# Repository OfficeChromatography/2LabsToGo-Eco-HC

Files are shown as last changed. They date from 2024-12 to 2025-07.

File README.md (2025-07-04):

# 2LabsToGo-Eco-HC

<u>Reference:</u> Schwack, W., Schmidt, J., Nimmerfroh, T. et al. Do-it-yourself, stand-alone, 
open-source nebulizer for derivatizations and bioassays in planar chromatography. 
JPC-J Planar Chromat (2025). https://doi.org/10.1007/s00764-025-00358-8

The repository contains the files for upgrading 2LabsToGo-Eco
 (https://github.com/OfficeChromatography/2LabsToGo-Eco) for Humidity Control.

## Downloading 2LabsToGo-Eco-HC
On the Raspberry Pi, open a new terminal and change to the directory Downloads
```bash
	cd ~/Downloads
```
Clone the 2LabsToG-Eco-HC repository from Github
```
	sudo git clone https://github.com/OfficeChromatography/2LabsToGo-Eco-HC.git
````

## Updating the firmware
The Marlin firmware and a built hex file are available in the folder Firmware-update.<br>
Copy the firmware hex file (firmware_2LabsToGo-Eco.hex) to the folder 2LabsToGo-Eco-Firmware.
```
	sudo cp -R ~/Downloads/2LabsToGo-Eco-HC/Firmware-update ~/2LabsToGo-Eco/2LabsToGo-Eco-Firmware
````
Change to the firmware folder
```
	cd ~/2LabsToGo-Eco/2LabsToGo-Eco-Firmware
````
Place the 2x4 jumper block onto the "ISP to PI" pins of the mainboard!<br> <br>
Execute the avrdude command
```
	sudo avrdude -p atmega2560 -C avrdude_gpio.conf -c 2LabsToGo -v -U flash:w:firmware_2LabsToGo-Eco.hex:i
````
Remove the jumper block from the "ISP to Pi" pins.<br>

## PID Tuning
After flashing the new firmware, the PID tuning must be performed again:<br>
•	In the software (Connection tab), connect the board.<br>
•	Insert the multifunctional plateholder and connect the plug.<br>
•	Connect the Mini-Incubator to the board.<br>
•	Send the following Gcodes and wait for finishing the tuning process
````
	M303 E-1 C8 S90 U  (for plateholder)
	M303 E0 C8 S40 U  (for Mini-Incubator)
````

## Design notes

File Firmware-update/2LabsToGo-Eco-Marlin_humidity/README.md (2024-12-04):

# OC-Control 
A Marlin 2.0 3D Printer based Firmware

## Marlin 2.0

Marlin 2.0 takes this popular RepRap firmware to the next level by adding support for much faster 32-bit and ARM-based boards while improving support for 8-bit AVR boards. Read about Marlin's decision to use a "Hardware Abstraction Layer" below.

Download earlier versions of Marlin on the [Releases page](https://github.com/MarlinFirmware/Marlin/releases).

## Building OC-Control

To build OC-Control [PlatformIO](http://docs.platformio.org/en/latest/ide.html#platformio-ide) is preferred. Detailed build and install instructions are posted at:

  - [Installing Marlin (VSCode)](http://marlinfw.org/docs/basics/install_platformio_vscode.html).

If you need more help, follow our [instruction_visualstudio-code](https://github.com/OfficeChromatography/OCLab3/blob/master/instruction_visualstudio-code.pdf), available above in the OCLab3 folder.

# OC-Manager 3 SOFTWARE
OC-Manager 3 installation 
[OC-Manager3](https://github.com/OfficeChromatography/OCLab3-Software)

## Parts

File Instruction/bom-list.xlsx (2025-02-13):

Parts | Amount | Exemplary seller | Euro (+VAT)
Fan MECHATRONICS MD4028V12B-RSR, 12VDC, 40mm L x 40mm H, 24.3cfm (0.680m³/min) (Digikey No. 1570-1126-ND) | 1 | Digikey | 11.31
Jumper Wire Male to Female 12.00" (304.80mm) 26 AWG, pack of 10, diff. colors (Digikey No. 2183-4567-ND) | 1 | Digikey | 2.81
Plexiglas 215 mm x 190 mm x 3 mm (front_215x190.dxf) | 1 | kunstoffplattenonline.de | 5.00
Round magnets, Ø 8 mm x 3 mm | 10 | supermagnete.de | 4.45
Superglue | 1 | local workshop | 4.90
Screw M3x40 | 4 | local workshop | 0.80
Nut M3 | 4 | local workshop | 0.60
Double-Sided Adhesive Tape tape, 6 mm, 50 cm needed | 1 | local workshop | 6.50
Eurostyle terminal strip with screws, 0.5 - 1.5 mm2 | 1 | local workshop | 2.00
 |  |  | 38.37

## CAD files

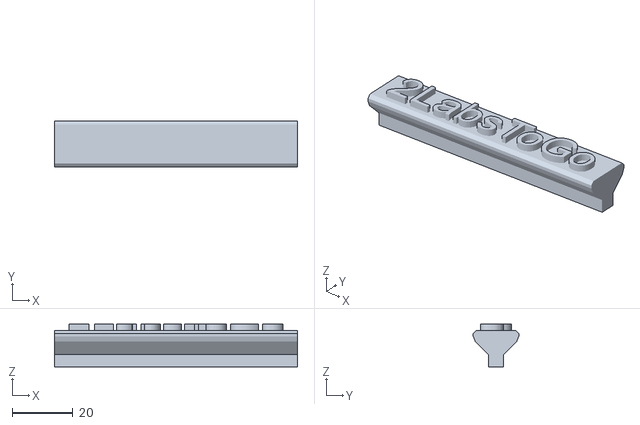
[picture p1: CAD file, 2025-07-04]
3D-parts/STL/front_holder.stl
80.0 x 15.0 x 14.0

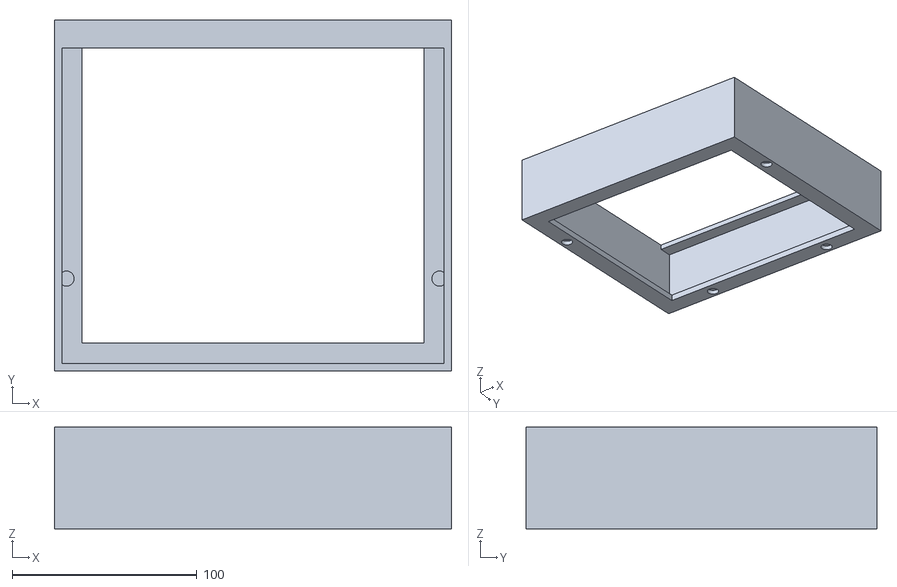
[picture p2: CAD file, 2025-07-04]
3D-parts/STL/front-extension.stl
215.0 x 190.0 x 55.0

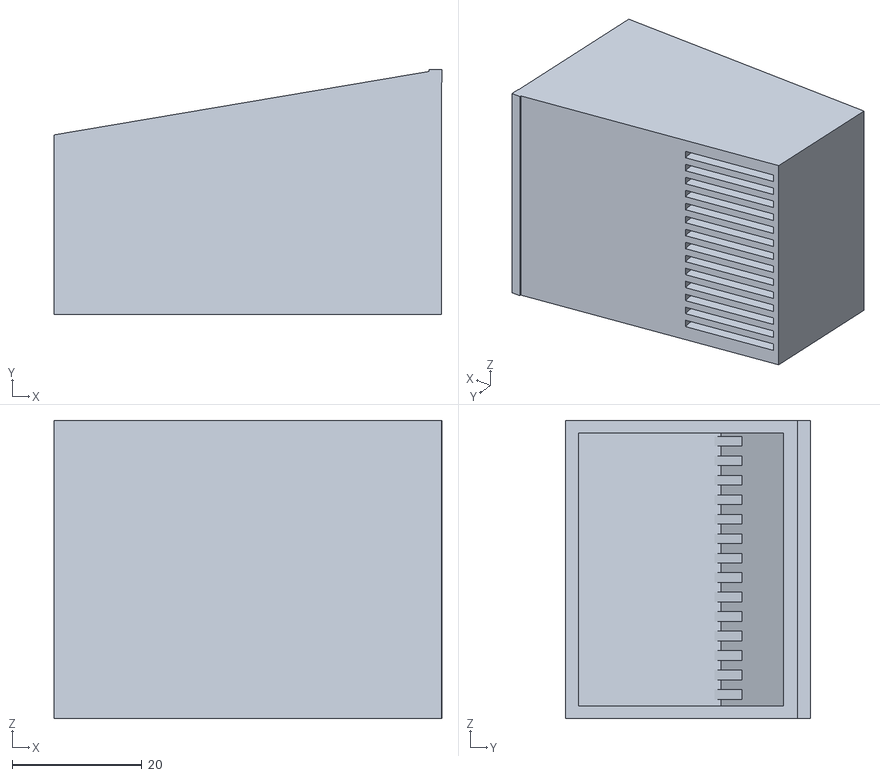
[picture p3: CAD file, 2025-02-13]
3D-parts/STL/humidity_control_drawer.stl
59.8 x 37.8 x 46.0

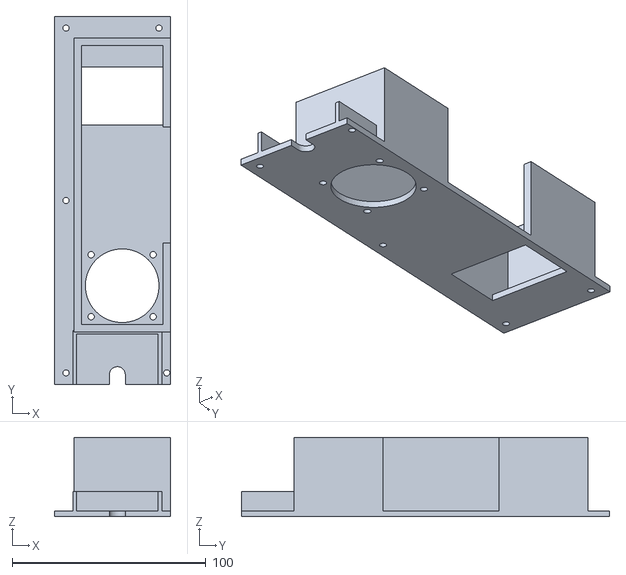
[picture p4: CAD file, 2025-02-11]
3D-parts/STL/humidity_control_box.stl
60.0 x 190.0 x 41.0

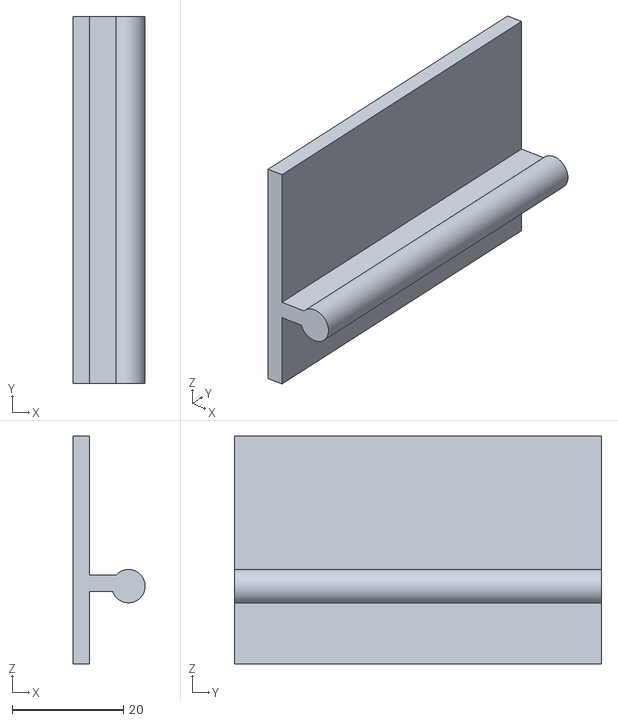
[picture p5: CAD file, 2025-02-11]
3D-parts/STL/humidity_control_drawer-handle.stl
13.0 x 66.0 x 41.0

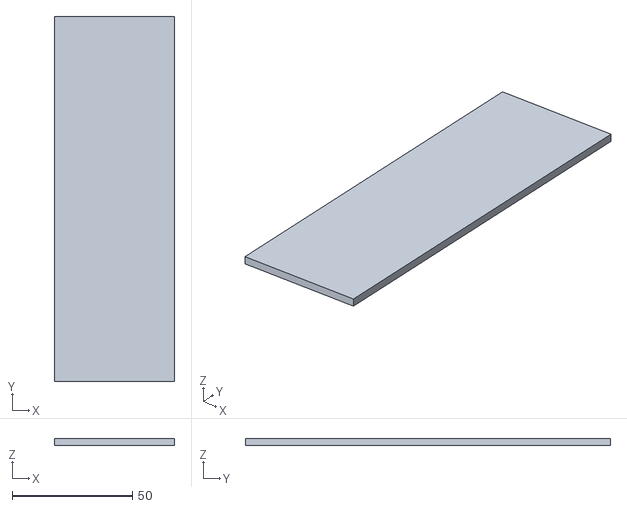
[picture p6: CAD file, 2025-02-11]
3D-parts/STL/humidity_control_box-lid.stl
50.0 x 152.0 x 3.00

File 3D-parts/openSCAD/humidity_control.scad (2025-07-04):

//humidity control 2LabsToGo-Eco

$fn=80;
h=38; //box height
hf=28; //fan height

box();
//lid();
//drawer();
//drawer_handle();
//front_extension();

module box() {
difference() {
    union() {
        cube([60, 190, 3]);
        translate([10, 20+7, 3]) cube([47, 4, h]);
        translate([10, 20+7, 3]) cube([4, 155-7, h]);
        translate([60-4, 20+7, 3]) cube([4, 155-7, h]);
        translate([10, 145+30, 3]) cube([50, 4, h]);
        
        //z1 motor cover
        translate([32.5-21-2, 0, 3]) cube([2, 28, 10]);
       translate([32.5+21, 0, 3]) cube([2, 28, 10]); 
        translate([32.5-21-2, 26, 3]) cube([44, 2, 10]);
    }
    //cutouts
    //cutout z1 spindle
       translate([32.5, 5.1, -1]) cylinder(d=8.2, h=5);
       translate([32.5-8.2/2, -1, -1]) cube([8.2, 6.1, 5]);
    //cutout suction opening
    translate([10+4, 134, -1]) cube([42, 30, 6]);
    //cutout fan
    translate([35, 30+21, -1]) cylinder(d=38, h=5);
    //holes fan screws
    translate([10+3+4+2, 30+21-16, -1]) cylinder(d=3.3, h=6);
    translate([10+3+4+32+2, 30+21-16, -1]) cylinder(d=3.3, h=6);
    translate([10+3+4+2, 30+21+16, -1]) cylinder(d=3.3, h=6);
    translate([10+3+4+32+2, 30+21+16, -1]) cylinder(d=3.3, h=6);
    //cutout drawer
    rotate([90, 0, 90]) translate([30+20+23, 3, 55])  cutout_drawer(); 
    //holes for screws
    for (i=[0:2])
    translate([6, 6+i*89, -1]) cylinder(d=3.2, h=5);
    translate([60-2, 6, -1]) cylinder(d=3.2, h=5);
    translate([60-6, 190-6, -1]) cylinder(d=3.2, h=5);
    }
}

module lid() {
    cube([50, 155+3-6, 3]);
}

module drawer() {
    difference() {
        linear_extrude(height = 46, scale = 1) 
    polygon(points=[[0,0],[0,hf-0.3],[60-0.3,h-0.2], [60-0.3,0]]);
        translate([2, 2, 2])
        linear_extrude(height = 46-4, scale = 1)  polygon(points=[[0,0],[0,hf-6],[60,h-6], [60,0]]);
   
    a=(h-hf)/60; //arctan
    b=a*180/3.14;  //rad in °
    //1.5 mm slits
    for(x=[3:3:42])
    translate([2, hf-5, x]) rotate([0, 0, b]) cube([20, 6, 1.5]);
    //1 mm slits
    //for(x=[3:2:44])
    //translate([2, hf-5, x]) rotate([0, 0, b]) cube([20, 6, 1]); 
    }
    translate([60-2.2, h-2.2, 0]) cube([2, 2, 46 ]);
}

module cutout_drawer() {
    linear_extrude(height = 10, scale = 1) 
    polygon(points=[[0,0],[0,h],[60,h], [60,0]]);
}

module drawer_handle() {
    translate([95-3-3+3, -3, 0]) cube([3, 66, h+3]);
    translate([95-3-3+3, -3, 13]) cube([10, 66, 3]);
    translate([95-3+10, -3, 14]) rotate([-90, 0, 0]) cylinder(d=6, h=66);
}

module fan( ) {
    difference() {
    hull() {
        translate([3, 3, 0]) cylinder(d=6, h=28);
        translate([40-3, 3, 0]) cylinder(d=6, h=28);
        translate([3, 40-3, 0]) cylinder(d=6, h=28);
        translate([40-3, 40-3, 0]) cylinder(d=6, h=28);
    }
    translate([20, 20, -1]) cylinder(d=38, h=42);
}
translate([20, 20, 0]) cylinder(d=12, h=28);
$fn=120;

translate([20, 20, 0])
linear_extrude(height = 28, center = false, convexity = 10, twist = 360, $fn = 100)
translate([5, 0, 0])
square([13, 1]);

translate([20, 20, 0]) rotate([0, 0, 120])
linear_extrude(height = 28, center = false, convexity = 10, twist = 360, $fn = 100)
translate([5, 0, 0])
square([13, 1]);

translate([20, 20, 0]) rotate([0, 0, 240])
linear_extrude(height = 28, center = false, convexity = 10, twist = 360, $fn = 100)
translate([5, 0, 0])
square([13, 1]);

}

module front_extension() {
    difference() {
    union() {
        cube([215, 190, 5]);
        cube([4, 190, 55]);
        cube([215, 4, 55]); 
        translate([215-4, 0, 0]) cube([4, 190, 55]);    
        translate([0, 190-4, 4]) cube([215, 4, 55-4]);
        translate([0, 190-15, 55-4]) cube([215, 15, 4]);
        }
    translate([15, 15, -1]) cube([215-2*15, 190-2*15, 7]);
    //cutout magnets
        translate([50, 190-6.5, 0]) cylinder(d1=9, d2=8.2, h=3.2);
        translate([215-50, 190-6.5, 0]) cylinder(d1=9, d2=8.2, h=3.2);
        translate([50, 190-6.5, 5-1.5]) cylinder(d=9, h=4);
        translate([215-50, 190-6.5, 5-1.5]) cylinder(d=9, h=4);
        
        translate([6.5, 50, 0]) cylinder(d1=9, d2=8.2, h=3.2);
        translate([215-6.5, 50, 0]) cylinder(d1=9, d2=8.2, h=3.2);
        translate([6.5, 50, 5-1.5]) cylinder(d=8.2, h=4);
        translate([215-6.5, 50, 5-1.5]) cylinder(d=8.2, h=4);
    }
}

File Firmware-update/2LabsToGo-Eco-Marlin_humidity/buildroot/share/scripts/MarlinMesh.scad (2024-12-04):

 /**************************************\
 *                                      *
 *   OpenSCAD Mesh Display              *
 *   by Thinkyhead - April 2017         *
 *                                      *
 *   Copy the grid output from Marlin,  *
 *   paste below as shown, and use      *
 *   OpenSCAD to see a visualization    *
 *   of your mesh.                      *
 *                                      *
 \**************************************/

$t = 0.15; // comment out during animation!
X = 0; Y = 1;
L = 0; R = 1; F = 2; B = 3;

//
// Sample Mesh - Replace with your own
//
measured_z = [
  [ -1.20, -1.13, -1.09, -1.03, -1.19 ],
  [ -1.16, -1.25, -1.27, -1.25, -1.08 ],
  [ -1.13, -1.26, -1.39, -1.31, -1.18 ],
  [ -1.09, -1.20, -1.26, -1.21, -1.18 ],
  [ -1.13, -0.99, -1.03, -1.06, -1.32 ]
];

//
// An offset to add to all points in the mesh
//
zadjust     = 0;

//
// Mesh characteristics
//
bed_size = [ 200, 200 ];

mesh_inset  = [ 10, 10, 10, 10 ]; // L, F, R, B

mesh_bounds = [
  [ mesh_inset[L], mesh_inset[F] ],
  [ bed_size[X] - mesh_inset[R], bed_size[Y] - mesh_inset[B] ]
];

mesh_size = mesh_bounds[1] - mesh_bounds[0];

                      // NOTE: Marlin meshes already subtract the probe offset
NAN         = 0;      // Z to use for un-measured points

//
// Geometry
//

max_z_scale   = 100;   // Scale at Time 0.5
min_z_scale   = 10;    // Scale at Time 0.0 and 1.0
thickness     = 0.5;   // thickness of the mesh triangles
tesselation   = 1;     // levels of tesselation from 0-2
alternation   = 2;     // direction change modulus (try it)

//
// Appearance
//

show_plane    = true;
show_labels   = true;
show_coords   = true;
arrow_length  = 5;

label_font_lg = "Arial";
label_font_sm = "Arial";
mesh_color    = [1,1,1,0.5];
plane_color   = [0.4,0.6,0.9,0.6];

//================================================ Derive useful values

big_z = max_2D(measured_z,0);
lil_z = min_2D(measured_z,0);

mean_value = (big_z + lil_z) / 2.0;

mesh_points_y = len(measured_z);
mesh_points_x = len(measured_z[0]);

xspace = mesh_size[X] / (mesh_points_x - 1);
yspace = mesh_size[Y] / (mesh_points_y - 1);

// At $t=0 and $t=1 scale will be 100%
z_scale_factor = min_z_scale + (($t > 0.5) ? 1.0 - $t : $t) * (max_z_scale - min_z_scale) * 2;

//
// Min and max recursive functions for 1D and 2D arrays
// Return the smallest or largest value in the array
//
function some_1D(b,i) = (i<len(b)-1) ? (b[i] && some_1D(b,i+1)) : b[i] != 0;
function some_2D(a,j) = (j<len(a)-1) ? some_2D(a,j+1) : some_1D(a[j], 0);
function min_1D(b,i) = (i<len(b)-1) ? min(b[i], min_1D(b,i+1)) : b[i];
function min_2D(a,j) = (j<len(a)-1) ? min_2D(a,j+1) : min_1D(a[j], 0);
function max_1D(b,i) = (i<len(b)-1) ? max(b[i], max_1D(b,i+1)) : b[i];
function max_2D(a,j) = (j<len(a)-1) ? max_2D(a,j+1) : max_1D(a[j], 0);

//
// Get the corner probe points of a grid square.
//
// Input  : x,y grid indexes
// Output : An array of the 4 corner points
//
function grid_square(x,y) = [
  [x * xspace, y * yspace, z_scale_factor * (measured_z[y][x] - mean_value)],
  [x * xspace, (y+1) * yspace, z_scale_factor * (measured_z[y+1][x] - mean_value)],
  [(x+1) * xspace, (y+1) * yspace, z_scale_factor * (measured_z[y+1][x+1] - mean_value)],
  [(x+1) * xspace, y * yspace, z_scale_factor * (measured_z[y][x+1] - mean_value)]
];

// The corner point of a grid square with Z centered on the mean
function pos(x,y,z) = [x * xspace, y * yspace, z_scale_factor * (z - mean_value)];

//
// Draw the point markers and labels
//
module point_markers(show_home=true) {
  // Mark the home position 0,0
  if (show_home)
    translate([1,1]) color([0,0,0,0.25])
      cylinder(r=1, h=z_scale_factor, center=true);

  for (x=[0:mesh_points_x-1], y=[0:mesh_points_y-1]) {
    z = measured_z[y][x] - zadjust;
    down = z < mean_value;
    xyz = pos(x, y, z);
    translate([ xyz[0], xyz[1] ]) {

      // Show the XY as well as the Z!
      if (show_coords) {
        color("black")
        translate([0,0,0.5]) {
          $fn=8;
          rotate([0,0]) {
            posx = floor(mesh_bounds[0][X] + x * xspace);
            posy = floor(mesh_bounds[0][Y] + y * yspace);
            text(str(posx, ",", posy), 2, label_font_sm, halign="center", valign="center");
          }
        }
      }

      translate([ 0, 0, xyz[2] ]) {
        // Label each point with the Z
        v = z - mean_value;
        if (show_labels) {

          color(abs(v) < 0.1 ? [0,0.5,0] : [0.25,0,0])
          translate([0,0,down?-10:10]) {

            $fn=8;
            rotate([90,0])
              text(str(z), 6, label_font_lg, halign="center", valign="center");

            if (v)
              translate([0,0,down?-6:6]) rotate([90,0])
                text(str(down || !v ? "" : "+", v), 3, label_font_sm, halign="center", valign="center");
          }
        }

        // Show an arrow pointing up or down
        if (v) {
          rotate([0, down ? 180 : 0]) translate([0,0,-1])
            cylinder(
              r1=0.5,
              r2=0.1,
              h=arrow_length, $fn=12, center=1
            );
        }
        else
          color([1,0,1,0.4]) sphere(r=1.0, $fn=20, center=1);
      }
    }
  }
}

//
// Split a square on the diagonal into
// two triangles and render them.
//
//     s : a square
//   alt : a flag to split on the other diagonal
//
module tesselated_square(s, alt=false) {
  add = [0,0,thickness];
  p1 = [
    s[0], s[1], s[2], s[3],
    s[0]+add, s[1]+add, s[2]+add, s[3]+add
  ];
  f1 = alt
      ? [ [0,1,3], [4,5,1,0], [4,7,5], [5,7,3,1], [7,4,0,3] ]
      : [ [0,1,2], [4,5,1,0], [4,6,5], [5,6,2,1], [6,4,0,2] ];
  f2 = alt
      ? [ [1,2,3], [5,6,2,1], [5,6,7], [6,7,3,2], [7,5,1,3] ]
      : [ [0,2,3], [4,6,2,0], [4,7,6], [6,7,3,2], [7,4,0,3] ];

  // Use the other diagonal
  polyhedron(points=p1, faces=f1);
  polyhedron(points=p1, faces=f2);
}

/**
 * The simplest mesh display
 */
module simple_mesh(show_plane=show_plane) {
  if (show_plane) color(plane_color) cube([mesh_size[X], mesh_size[Y], thickness]);
  color(mesh_color)
    for (x=[0:mesh_points_x-2], y=[0:mesh_points_y-2])
      tesselated_square(grid_square(x, y));
}

/**
 * Subdivide the mesh into smaller squares.
 */
module bilinear_mesh(show_plane=show_plane,tesselation=tesselation) {
  if (show_plane) color(plane_color) translate([-5,-5]) cube([mesh_size[X]+10, mesh_size[Y]+10, thickness]);

  if (some_2D(measured_z, 0)) {

    tesselation = tesselation % 4;
    color(mesh_color)
    for (x=[0:mesh_points_x-2], y=[0:mesh_points_y-2]) {
      square = grid_square(x, y);
      if (tesselation < 1) {
        tesselated_square(square,(x%alternation)-(y%alternation));
      }
      else {
        subdiv_4 = subdivided_square(square);
        if (tesselation < 2) {
          for (i=[0:3]) tesselated_square(subdiv_4[i],i%alternation);
        }
        else {
          for (i=[0:3]) {
            subdiv_16 = subdivided_square(subdiv_4[i]);
            if (tesselation < 3) {
              for (j=[0:3]) tesselated_square(subdiv_16[j],j%alternation);
            }
            else {
              for (j=[0:3]) {
                subdiv_64 = subdivided_square(subdiv_16[j]);
                if (tesselation < 4) {
                  for (k=[0:3]) tesselated_square(subdiv_64[k]);
                }
              }
            }
          }
        }
      }
    }

  }
}

//
// Subdivision helpers
//
function ctrz(a) = (a[0][2]+a[1][2]+a[3][2]+a[2][2])/4;
function avgx(a,i) = (a[i][0]+a[(i+1)%4][0])/2;
function avgy(a,i) = (a[i][1]+a[(i+1)%4][1])/2;
function avgz(a,i) = (a[i][2]+a[(i+1)%4][2])/2;

//
// Convert one square into 4, applying bilinear averaging
//
// Input  : 1 square (4 points)
// Output : An array of 4 squares
//
function subdivided_square(a) = [
  [ // SW square
    a[0],                          // SW
    [a[0][0],avgy(a,0),avgz(a,0)], // CW
    [avgx(a,1),avgy(a,0),ctrz(a)], // CC
    [avgx(a,1),a[0][1],avgz(a,3)]  // SC
  ],
  [ // NW square
    [a[0][0],avgy(a,0),avgz(a,0)], // CW
    a[1],                          // NW
    [avgx(a,1),a[1][1],avgz(a,1)], // NC
    [avgx(a,1),avgy(a,0),ctrz(a)]  // CC
  ],
  [ // NE square
    [avgx(a,1),avgy(a,0),ctrz(a)], // CC
    [avgx(a,1),a[1][1],avgz(a,1)], // NC
    a[2],                          // NE
    [a[2][0],avgy(a,0),avgz(a,2)]  // CE
  ],
  [ // SE square
    [avgx(a,1),a[0][1],avgz(a,3)], // SC
    [avgx(a,1),avgy(a,0),ctrz(a)], // CC
    [a[2][0],avgy(a,0),avgz(a,2)], // CE
    a[3]                           // SE
  ]
];


//================================================ Run the plan

translate([-mesh_size[X] / 2, -mesh_size[Y] / 2]) {
  $fn = 12;
  point_markers();
  bilinear_mesh();
}

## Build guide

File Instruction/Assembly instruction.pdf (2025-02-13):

Assembly instruction

Materials | Qty
Axial fan, 40x28 mm, 12 V, Digikey-No. 1570-1125-ND | 1
Screw M3x40 | 4
Nut M3 | 4
Black and red wires, 25 cm | 1 each
Jumper Wires, male-to-female, 30 cm, black, red, blue, green | 1 each
Eurostyle terminal strip with screws, 2 positions, 0.5 - 1.5 mm² | 1
Double-sided tape, 6 mm, 50 cm | 1
3D-printed humidity_control_box | 1
3D-printed humidity_control_box-lid | 1
3D-printed humidity_control_drawer | 1
3D-printed humidity_control_drawer-handle | 1
3D-printed front_extension | 1
3D-printed front_holder | 1
Round magnets, Ø 8mm x 3 mm | 10
Plexiglas front, 215 mm x 190 mm x 3 mm (front_215x190.dxf) | 1

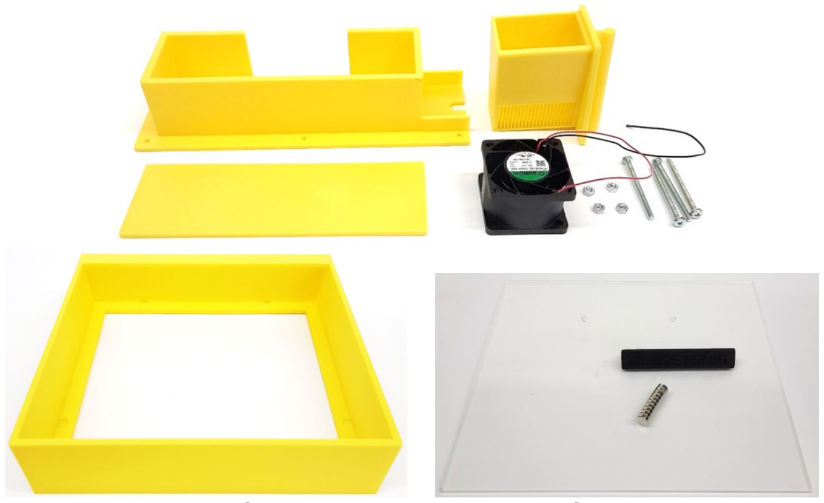
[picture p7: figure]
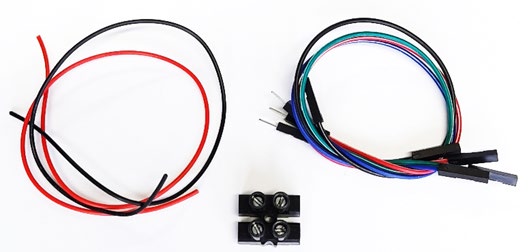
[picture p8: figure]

[3D parts here printed with yellow PLA]

Assembly

- Place the double-sided tape onto the edges of the humidity_control_box and cut the protruding tape.

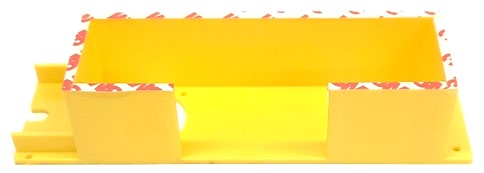
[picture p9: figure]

- Mount the fan with the M3x40 screws and M3 nuts inside the fan_holder, the cables and the label pointing downwards.

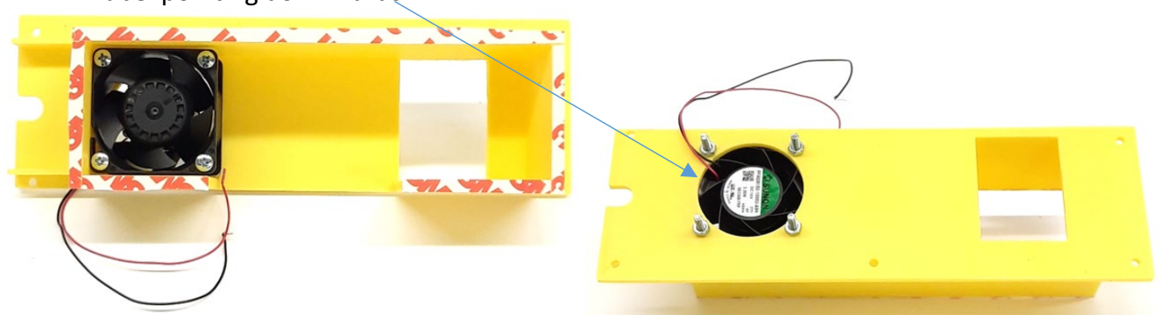
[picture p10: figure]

- Remove the protective film and press the humidity_control_box-lid onto the box.

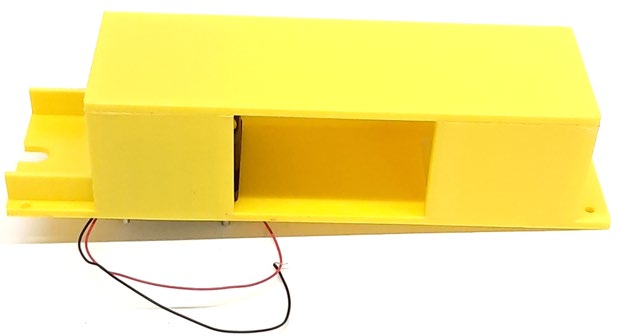
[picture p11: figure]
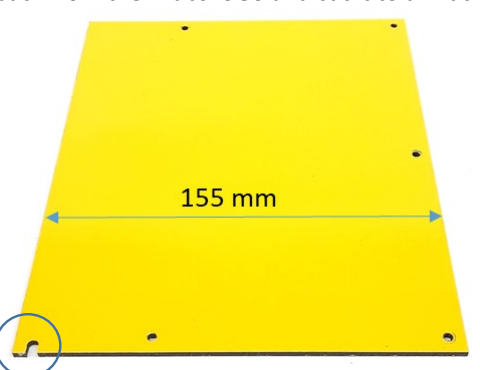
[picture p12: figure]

- Remove the panel_back from the 2LabsToGo and cut it to a width of 155 mm.

- Take the free 4-poles plug from the underside of the mainboard (external port) and connect one end of the red and black wires as shown (polarity important!). Connect the other ends to the 2-positions terminal strip.

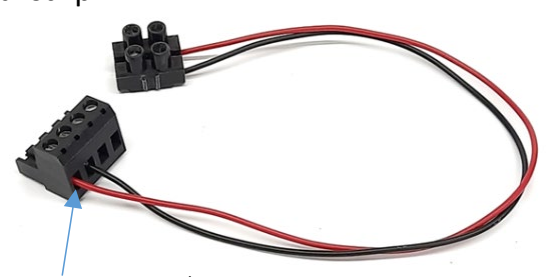
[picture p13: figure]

red at the 1st position!

- Insert the plug into the external port again and guide the cables with the terminal strip downwards to the back of the camera cabinet.
- To be on the safe side, check the polarity of the cables with a voltmeter (red to red, black to black). A wrong polarity will destroy the fan. Therefore, start the fan with 255 (Finecontrol in the software), when the voltmeter should show +12 V.

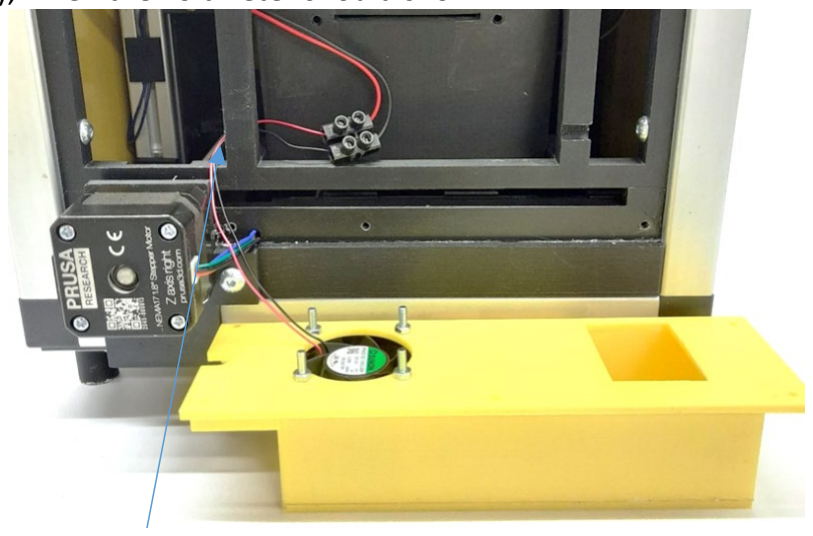
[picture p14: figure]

- Guide the fan cables behind the camera cabinet holder and connect them to the terminal strip (red to red, black to black!).

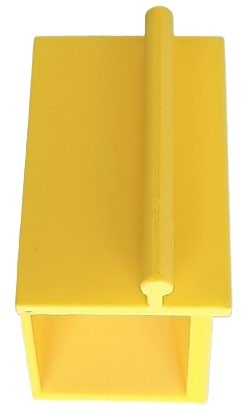
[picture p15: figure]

- Glue the drawer-handle onto the drawer.

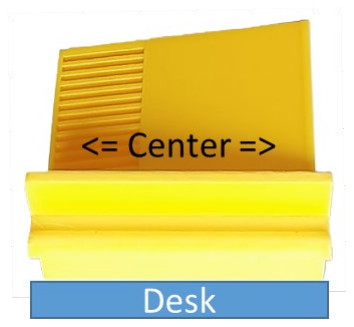
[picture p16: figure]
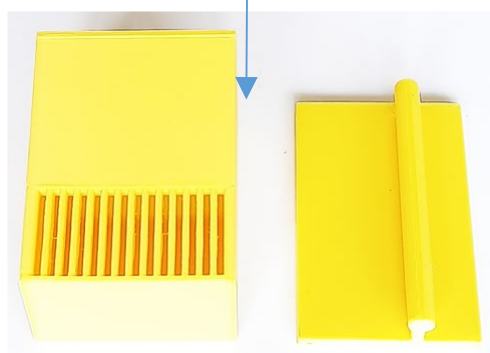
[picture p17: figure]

- With a 2.7-mm drill, drill two holes through the fan_holder into the frame_back.

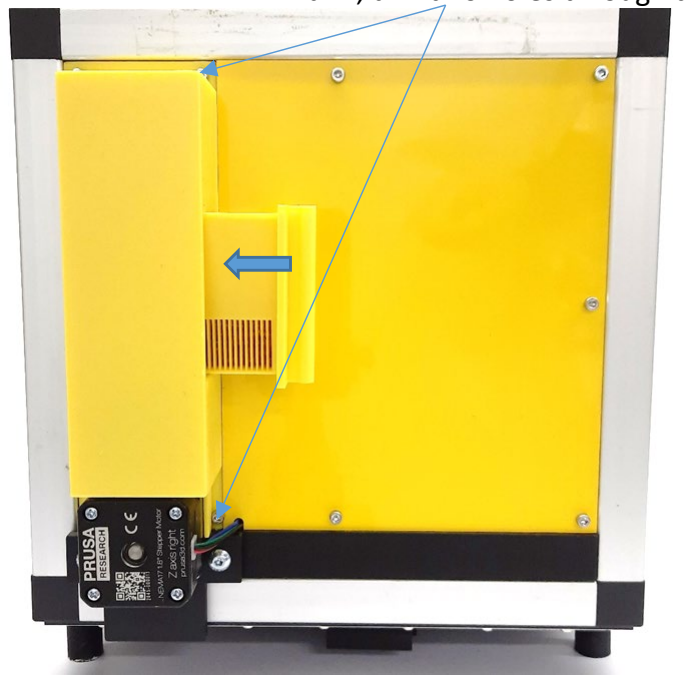
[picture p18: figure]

- Mount the fan_holder and the panel_back with ten M3x8 screws.
The cover_z1_motor is no longer required, it is included in the fan_holder.
- The 3D-printed silica_drawer is filled with silica gel orange/green (2-5 mm) and completely inserted into the cutout of the humidity_control_box.

An extension for the panel front is required to keep the 2LabsToGo-Eco closed during humidity control and plate development.

- As described in the 2LabsToGo-Eco Assembly Guide for the alupanel front, glue two round magnets onto the inner top side of the 3D-printed front_extension.

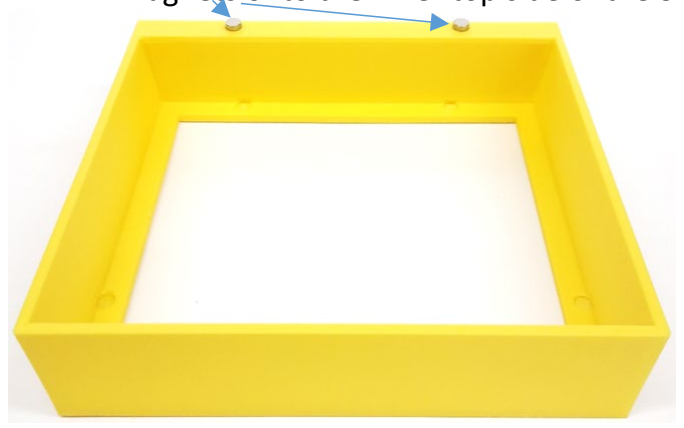
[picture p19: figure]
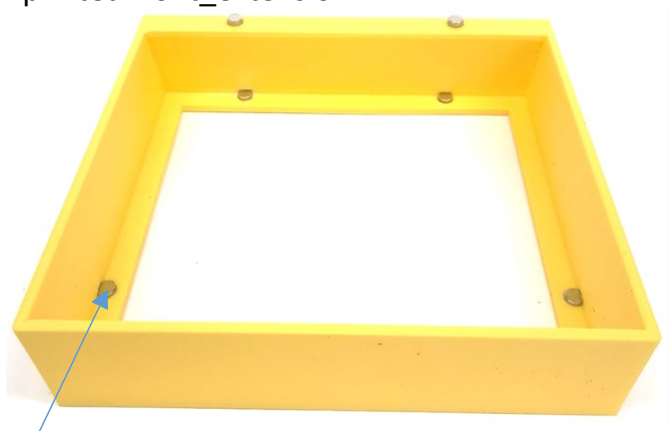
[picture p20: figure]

- Glue four round magnets in the round cutouts inside the front_extension.

- From a 1 mm thick cardboard, cut four squares of just under 6 mm, insert them into the four round cutouts in the front side of the extension and let attract four round magnets onto the cardboards.

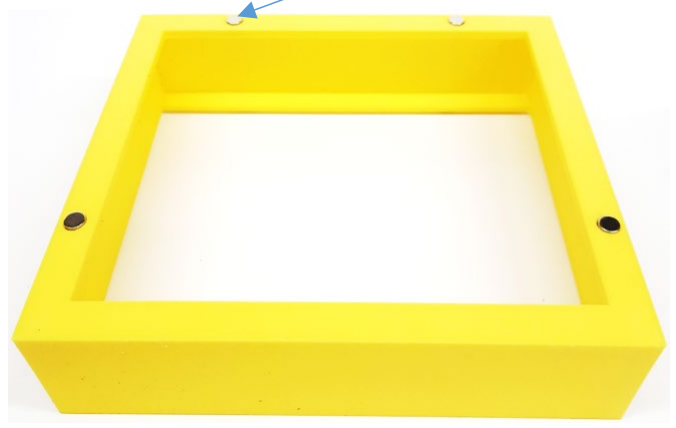
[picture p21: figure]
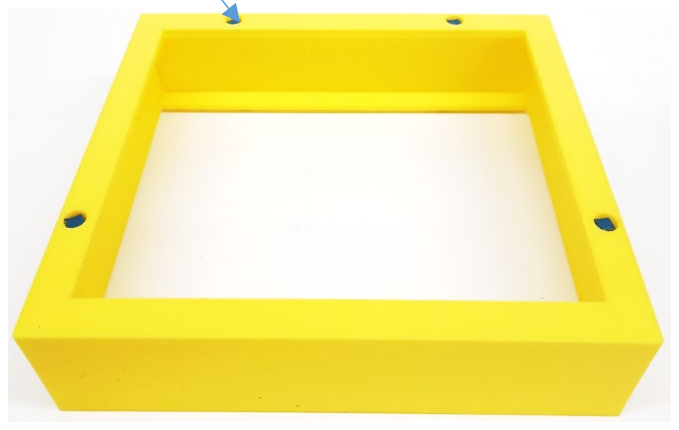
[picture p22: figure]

- Mount the 3D-printed front_holder with two M3x8 screws onto the Plexiglas front.

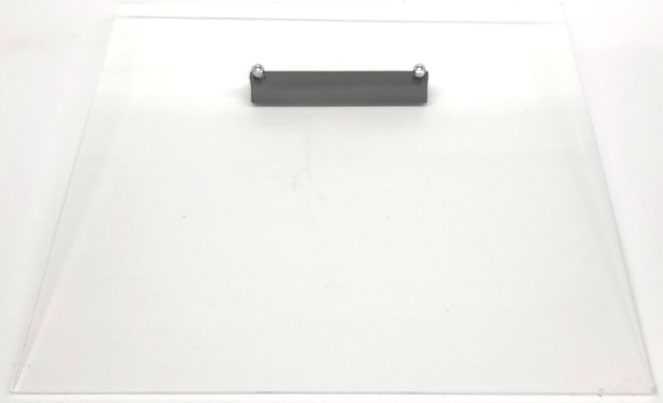
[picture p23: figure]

- Give a small drop of superglue onto the four magnets on the cardboards of the front_extension, place the Plexiglas front onto the front_extension while aligning it on the front_extension and press it down onto the magnets.
- Wait for hardening the glue, remove the Plexiglas front and the cardboards.

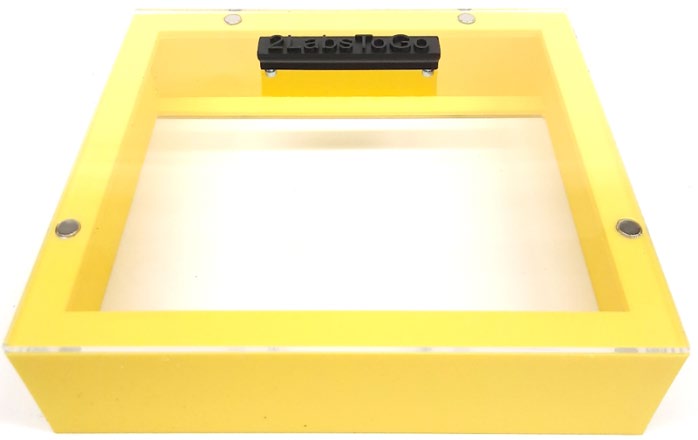
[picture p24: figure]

- Instead of the alupanel front, attach the front extension to the frame_front of the 2LabsToGo-Eco.

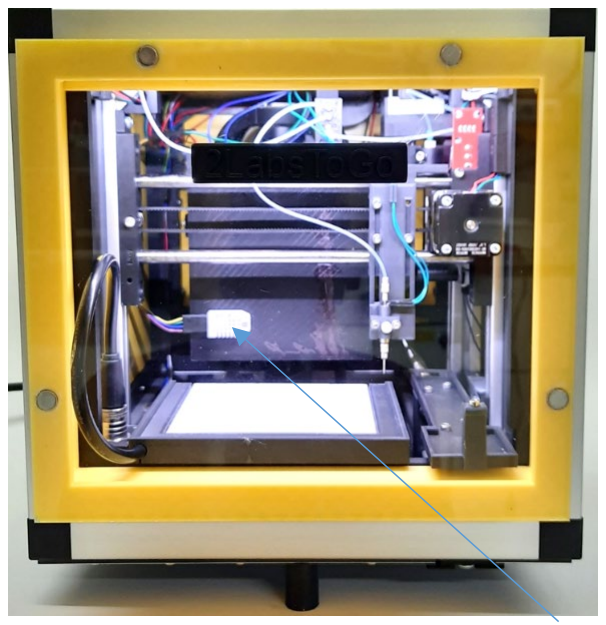
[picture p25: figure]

- Mount the DHT22 sensor (underside of the mainboard) onto the camera cabinet facing (small screw or double-sided tape) and connect it to the board with 30-cm jumper wire extensions.

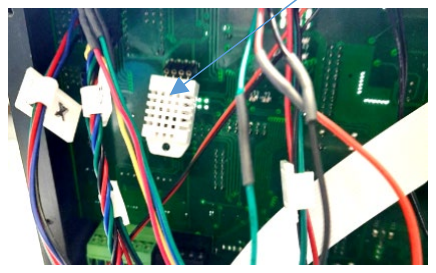
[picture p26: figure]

To use humidity control, firmware and software updates are required (https://github.com/OfficeChromatography/2LabsToGo-Eco-HC).

For updating the software and firmware, follow the instructions in the github README file.

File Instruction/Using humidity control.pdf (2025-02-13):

Using humidity control

Starting/Stopping humidity control in the 2LabsToGo-Eco-Software

In the side bar menu “Finecontrol” select “Humidity” and open it in a new tab (right click).

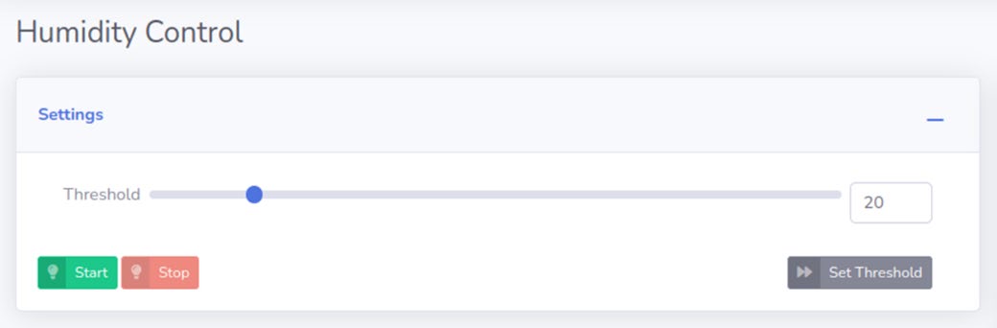
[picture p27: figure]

Set the humidity threshold to the desired value and click “Enable Sensor”. The fan will start running and stops if the set humidity value is reached. If the value is exceeded again, the fan restarts. The activities are displayed in the “Monitor” window.
The humidity control must be stopped before starting the development.
During the running humidity control, other processes like sample application or capturing images also cannot be started!

With both silica gel and molecular sieve, relative humidities down to 20 % can be reached.
Wet silica gel can be reactivated in an oven at 110 °C for four hours. Exceeding 110°C destroys the color indicator. Molecular sieve, however, must be reactivated at temperatures of ~300 °C.
